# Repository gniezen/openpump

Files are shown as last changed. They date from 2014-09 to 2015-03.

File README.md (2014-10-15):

# Openpump: the open source hardware syringe pump

[Openpump](http://www.openpump.org) is an open-source syringe pump that dispenses fluids over a set period of time. Syringe pumps are used to administer medication in hospitals, but also in laboratory environments performing chemical or biomedical research. Maybe you'd like to use syringe pump to extruding paste (e.g. chocolate) during 3D printing, or as part of a bioprinter when printing with biological materials?

Openpump is a collaboratively designed general-purpose syringe pump platform that can be customised for different domains. Making the hardware design available under an open source license allows anyone to improve and contribute to the device design. It also enables the design to be modified for very specific use cases and makes the devices easy to repair.

## Setup

### Rendering the 3D parts

The mechanical/CAD design of Openpump is based on work by Bas Wijnen, Emily Hunt, Gerald Anzalone and Joshua Pearce of  [Michigan Tech Open Sustainaibility Lab](http://www.appropedia.org/Open-source_syringe_pump). The 3D-printed parts were designed in [OpenSCAD](http://www.openscad.org/). (To learn how to use OpenSCAD, see [the Openpump blog](http://blog.openpump.org/how-to-design-a-3d-printed-enclosure-for-your-product/)). To render the different 3D parts in `linear_actuator_v0.scad`:

* Install the [MOST SCAD libraries](https://github.com/mtu-most/most-scad-libraries) by downloading them as a zip file and adding to OpenSCAD path using `export OPENSCADPATH=`<*your local path*> (in `~/.profile` on Ubuntu), or using `File->Show Library Folder` to add them to your OpenSCAD library.
* Change `render_part()` to the 3D part you want to render. You need `end_motor` (1), `end_idler` (2), `carriage_syringe_pump` (4), `clamp_syringe_pump` (5) and `syringe_plunger_retainer` (7) at a minimum.
* Before printing the syringe holder (part 5, `clamp_syringe_pump`), set the variable `d_syringe` to the be the same as the diameter of the syringe body you're using.
* Before printing the motor end (part 1, `end_motor`) set the `motor` variable to the size of stepper motor you're using, e.g. `NEMA17`
* I had best results printing the idler end (part 2, `end_idler`) with support material.

### Building the mechanical design
The step-by-step build instructions with pictures are in the [Building the syringe pump guide](http://openpump.dozuki.com/c/Build_instructions).

### Building the electronics
To build the electronics, you need the following components:
* [Arduino Mega 2560](http://arduino.cc/en/Main/ArduinoBoardMega2560) (You can also use another Arduino, but you'll need something like the Sparkfun [ProtoScrewShield](https://www.sparkfun.com/products/9729) to connect the other components as the Gameduino 2 shield covers all the pins of the regular Arduino)
* [Gameduino 2](http://excamera.com/sphinx/gameduino2/), an open source hardware touchscreen (480x272 pixels) with embedded GPU
* [Pololu DRV8834](http://www.pololu.com/product/2134) Low Voltage Stepper Motor Driver Board (You're welcome to replace this with another board if you know what you're doing)
* [ELMA E37](http://www.leobodnar.com/shop/index.php?main_page=product_info&cPath=75&products_id=196) dual concentric rotary encoder (kinda optional, used for number entry)

Because the Mega2560 has its SPI pins in a different place, you need to make 3 wire hookups. Connect:
- pin 11 to pin 51 (MOSI)
- pin 12 to pin 50 (MISO)
- pin 13 to pin 52 (SCK)

You can solder these three wires directly to the pins underneath the Mega.

To view the circuit schematic (with breadboard views), use the awesome open source hardware design tool [Fritzing](http://fritzing.org/).

## Installing the firmware

To get the firmware running on your Arduino, have a look at the documentation in the [firmware](firmware/) folder. 

## Licenses

### Software and firmware
The software and firmware of this project is *Copyright (C) 2014 Swansea University* and made available under the GNU Affero General Public License (AGPL 3.0). See LICENSE.txt in the firmware folder for more information.

### Mechanical design
The CAD design file (linear_actuator_v0.scad) is *Copyright 2013 Michigan Technological University* and licensed under the [CC-BY-SA](Creative Commons Attribution-ShareAlike 4.0 International License) by Jerry Anzalone, developed as part of a project with the [Michigan Tech Open Sustainability Technology Research Group](http://www.appropedia.org/Category:MOST).

### Circuit schematics
The circuit schematics of this project are made available under the [CERN Open Hardware License](http://www.ohwr.org/projects/cernohl/wiki). See LICENSE.PDF in the schematics folder for more information.

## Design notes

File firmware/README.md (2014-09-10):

# Openpump: Firmware

## Setup

To get this up and running in your Arduino environment, you need two libraries:
- [Encoder](https://www.pjrc.com/teensy/td_libs_Encoder.html)
- [Gameduino 2](http://excamera.com/files/Gameduino2.zip)

Install it in the Arduino environment using the [official instructions](http://arduino.cc/en/Guide/Libraries).

## Working with Gameduino 2
If you want to create your own assets for Gameduino 2, follow the setup instructions below and also see the instruction on the [Gameduino 2 website](http://excamera.com/sphinx/gameduino2/code.html#gd2code). 

### Library setup
Prerequisites:
- Install PIL using `sudo pip install pil` 
- Install Gameduino 2 asset converter and Python libraries using `sudo pip install gameduino2`

Note: On Mac you can also install `sudo pip install pillow` and port Gameduino 2 to use Pillow instead of PIL: http://pillow.readthedocs.org/en/latest/porting-pil-to-pillow.html

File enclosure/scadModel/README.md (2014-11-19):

# OpenSCAD OpenPump Enclosure

This design makes use of the [Arduino OpenSCAD mounting library (v2.0)](http://www.thingiverse.com/thing:64008) by Kelly Egan.

To create the enclosure:

	enclosure(MEGA2560);

To create the lid:

	enclosureLid(MEGA2560);

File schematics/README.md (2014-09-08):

# Openpump: Circuit Schematics

Copyright Swansea University 2014.

This documentation describes Open Hardware and is licensed under the
CERN OHL v. 1.2.

You may redistribute and modify this documentation under the terms of the CERN OHL v.1.2. (http://ohwr.org/cernohl). This documentation is distributed WITHOUT ANY EXPRESS OR IMPLIED WARRANTY, INCLUDING OF MERCHANTABILITY, SATISFACTORY QUALITY AND FITNESS FOR A PARTICULAR PURPOSE. Please see the CERN OHL v.1.2 for applicable conditions

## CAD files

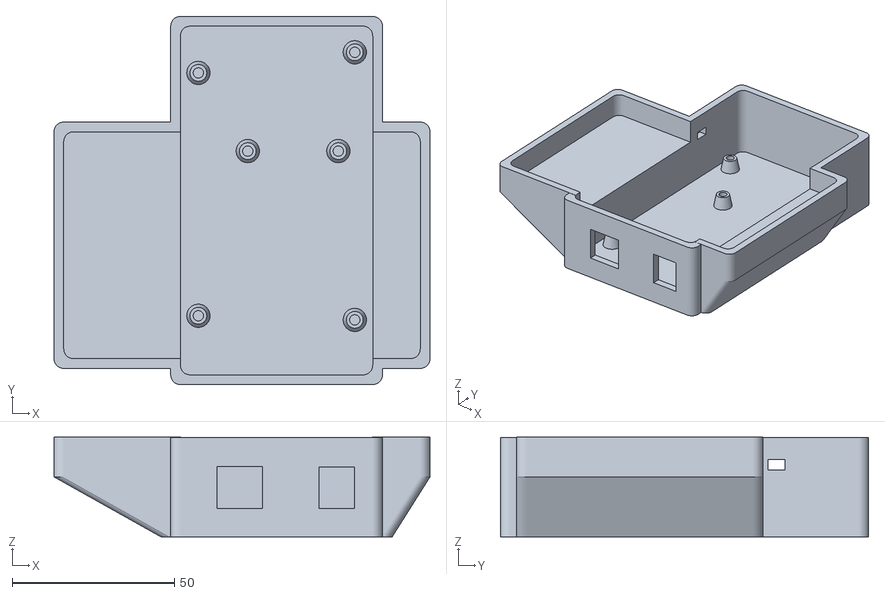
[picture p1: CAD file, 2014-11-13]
enclosure/scadModel/openPumpBox.stl
116.0 x 113.6 x 30.8

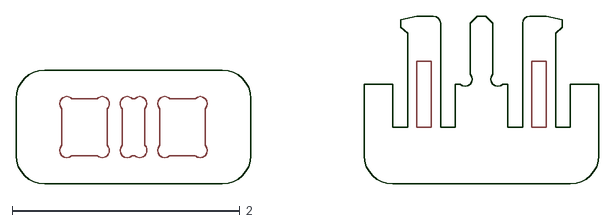
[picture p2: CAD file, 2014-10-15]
enclosure/snap.dxf
5.12 x 1.48

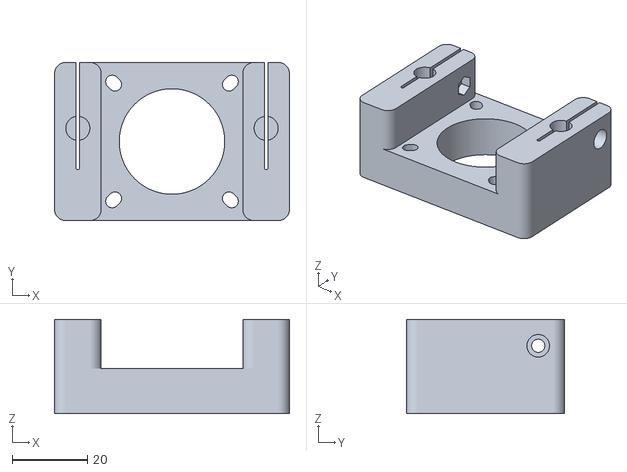
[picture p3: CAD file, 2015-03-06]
mechanical/1_end_motor.stl
62.4 x 42.0 x 25.0

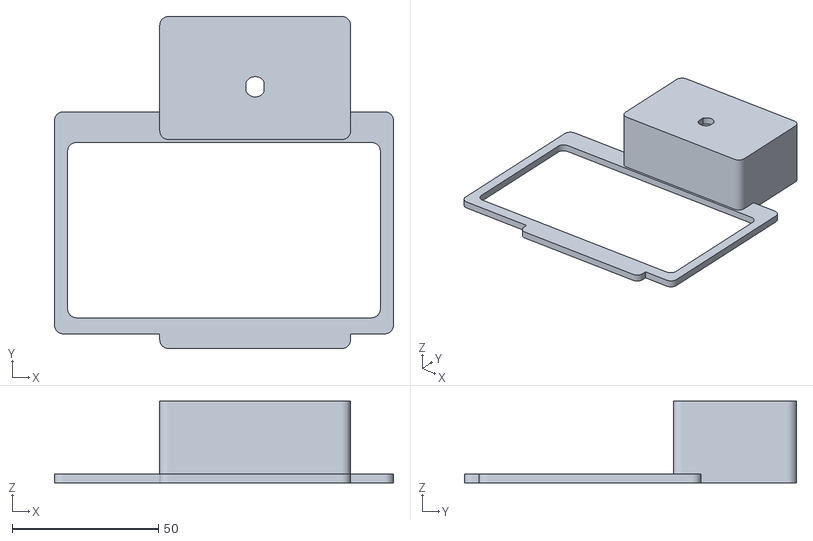
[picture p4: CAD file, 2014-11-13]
enclosure/scadModel/openPumpLid.stl
116.0 x 113.6 x 28.0

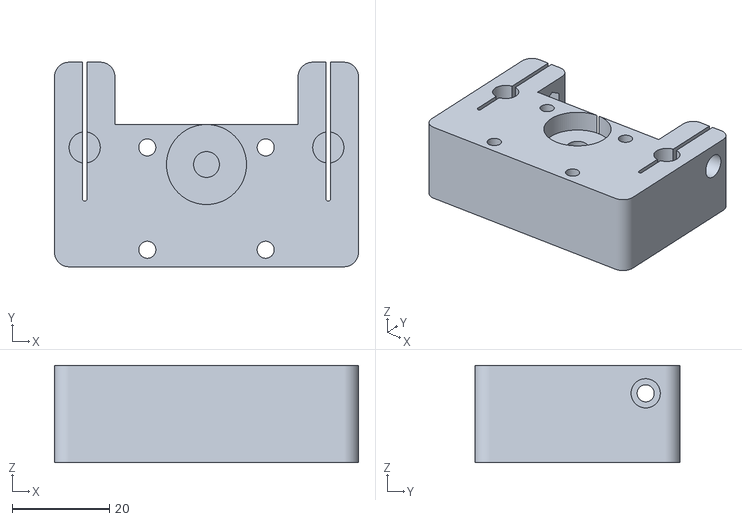
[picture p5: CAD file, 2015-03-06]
mechanical/2_end_idler.stl
62.4 x 42.0 x 20.0

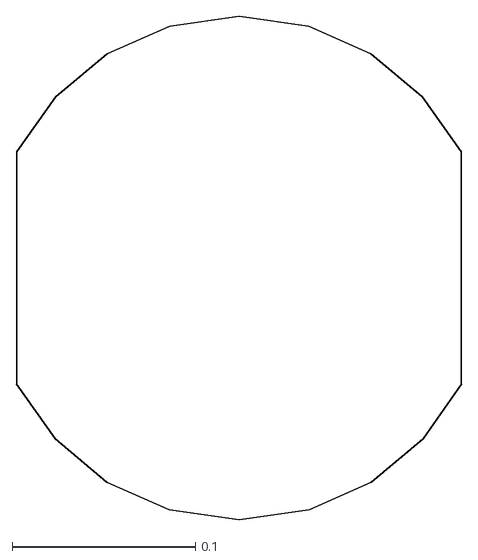
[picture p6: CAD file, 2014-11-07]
enclosure/scadModel/rotary.dxf
0.243 x 0.275

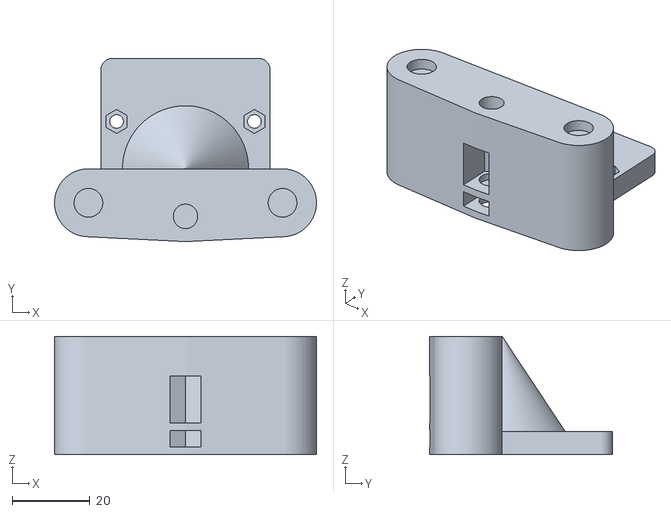
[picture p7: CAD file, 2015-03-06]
mechanical/4_carriage_syringe_pump.stl
67.5 x 47.2 x 30.5

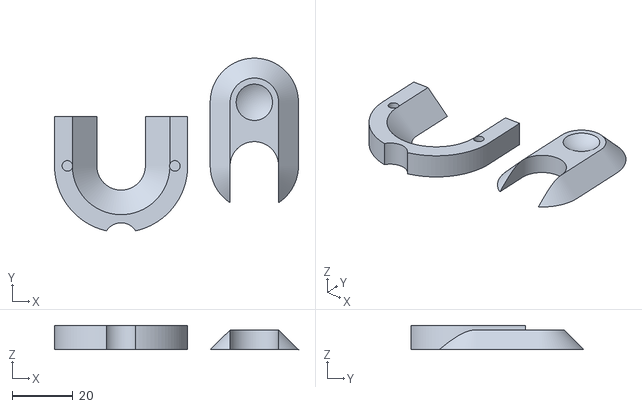
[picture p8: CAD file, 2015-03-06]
mechanical/7_syringe_plunger_retainer.stl
80.6 x 57.0 x 8.00

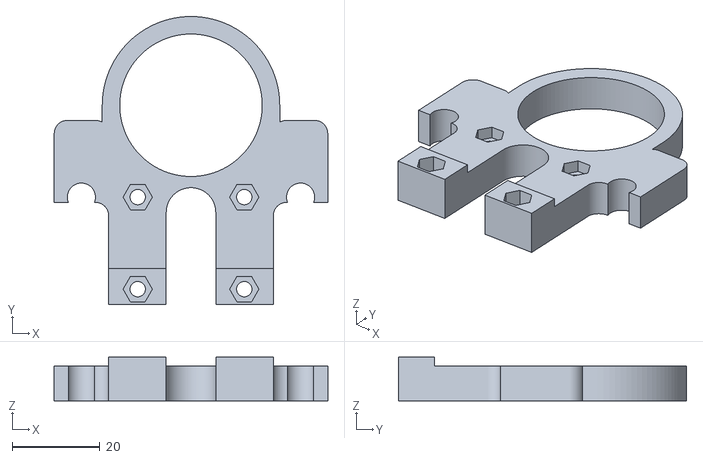
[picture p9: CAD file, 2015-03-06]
mechanical/5_clamp_syringe_pump.stl
62.4 x 65.7 x 10.0

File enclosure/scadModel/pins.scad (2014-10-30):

// Pin Connectors V3
// Tony Buser <tbuser@gmail.com>
// Modified by Emmett Lalish

object=4;//[0:pin,1:pinpeg,2:pinhole,4:nothing]
length=20;
diameter=8;
//Only affects pinhole
hole_twist=0;//[0:free,1:fixed]
//Only affects pinhole
hole_friction=0;//[0:loose,1:tight]
//Radial gap to help pins fit into tight holes
pin_tolerance=0.2;
//Extra gap to make loose hole
loose=0.3;
lip_height=3;
lip_thickness=1;
hf=hole_friction==0 ? false : true;
ht=hole_twist==0 ? false : true;

if(object==0)pin(h=length,r=diameter/2,lh=lip_height,lt=lip_thickness,t=pin_tolerance);
if(object==1)pinpeg(h=length,r=diameter/2,lh=lip_height,lt=lip_thickness,t=pin_tolerance);
if(object==2)pinhole(h=length,r=diameter/2,lh=lip_height,lt=lip_thickness,t=loose,
	tight=hf,fixed=ht);

module test() {
  tolerance = 0.3;
  
  translate([-12, 12, 0]) pinpeg(h=20);
  translate([12, 12, 0]) pintack(h=10);
  
  difference() {
    union() {
      translate([0, -12, 2.5]) cube(size = [59, 20, 5], center = true);
      translate([24, -12, 7.5]) cube(size = [12, 20, 15], center = true);
    }
    translate([-24, -12, 0]) pinhole(h=5, t=tolerance);
    translate([-12, -12, 0]) pinhole(h=5, t=tolerance, tight=false);
    translate([0, -12, 0]) pinhole(h=10, t=tolerance);
    translate([12, -12, 0]) pinhole(h=10, t=tolerance, tight=false);
    translate([24, -12, 15]) rotate([0, 180, 0]) pinhole(h=10, t=tolerance);
  }
}

module pinhole(h=10, r=4, lh=3, lt=1, t=0.3, tight=true, fixed=false) {
  // h = shaft height
  // r = shaft radius
  // lh = lip height
  // lt = lip thickness
  // t = extra tolerance for loose fit
  // tight = set to false if you want a joint that spins easily
  // fixed = set to true so pins can't spin
  
intersection(){
  union() {
	if (tight == true || fixed == true) {
      pin_solid(h, r, lh, lt);
	  translate([0,0,-t/2])cylinder(h=h+t, r=r, $fn=30);
	} else {
	  pin_solid(h, r+t/2, lh, lt);
	  translate([0,0,-t/2])cylinder(h=h+t, r=r+t/2, $fn=30);
	}
    
    
    // widen the entrance hole to make insertion easier
    //translate([0, 0, -0.1]) cylinder(h=lh/3, r2=r, r1=r+(t/2)+(lt/2),$fn=30);
  }
  if (fixed == true) {
	translate([-r*2, -r*0.75, -1])cube([r*4, r*1.5, h+2]);
  }
}}

module pin(h=10, r=4, lh=3, lt=1, t=0.2, side=false) {
  // h = shaft height
  // r = shaft radius
  // lh = lip height
  // lt = lip thickness
  // side = set to true if you want it printed horizontally

  if (side) {
    pin_horizontal(h, r, lh, lt, t);
  } else {
    pin_vertical(h, r, lh, lt, t);
  }
}

module pintack(h=10, r=4, lh=3, lt=1, t=0.2, bh=3, br=8.75) {
  // bh = base_height
  // br = base_radius
  
  union() {
    cylinder(h=bh, r=br);
    translate([0, 0, bh]) pin(h, r, lh, lt, t);
  }
}

module pinpeg(h=20, r=4, lh=3, lt=1, t=0.2) {
  union() {
    translate([0,-0.05, 0]) pin(h/2+0.1, r, lh, lt, t, side=true);
    translate([0,0.05, 0]) rotate([0, 0, 180]) pin(h/2+0.1, r, lh, lt, t, side=true);
  }
}

// just call pin instead, I made this module because it was easier to do the rotation option this way
// since openscad complains of recursion if I did it all in one module
module pin_vertical(h=10, r=4, lh=3, lt=1, t=0.2) {
  // h = shaft height
  // r = shaft radius
  // lh = lip height
  // lt = lip thickness

  difference() {
    pin_solid(h, r-t/2, lh, lt);
    
    // center cut
    translate([-lt*3/2, -(r*2+lt*2)/2, h/5+lt*3/2]) cube([lt*3, r*2+lt*2, h]);
    //translate([0, 0, h/4]) cylinder(h=h+lh, r=r/2.5, $fn=20);
    // center curve
    translate([0, 0, h/5+lt*3/2]) rotate([90, 0, 0]) cylinder(h=r*2, r=lt*3/2, center=true, $fn=20);
  
    // side cuts
    translate([-r*2, -r-r*0.75+t/2, -1]) cube([r*4, r, h+2]);
    translate([-r*2, r*0.75-t/2, -1]) cube([r*4, r, h+2]);
  }
}

// call pin with side=true instead of this
module pin_horizontal(h=10, r=4, lh=3, lt=1, t=0.2) {
  // h = shaft height
  // r = shaft radius
  // lh = lip height
  // lt = lip thickness
  translate([0, 0, r*0.75-t/2]) rotate([-90, 0, 0]) pin_vertical(h, r, lh, lt, t);
}

// this is mainly to make the pinhole module easier
module pin_solid(h=10, r=4, lh=3, lt=1) {
  union() {
    // shaft
    cylinder(h=h-lh, r=r, $fn=30);
    // lip
    // translate([0, 0, h-lh]) cylinder(h=lh*0.25, r1=r, r2=r+(lt/2), $fn=30);
    // translate([0, 0, h-lh+lh*0.25]) cylinder(h=lh*0.25, r2=r, r1=r+(lt/2), $fn=30);
    // translate([0, 0, h-lh+lh*0.50]) cylinder(h=lh*0.50, r1=r, r2=r-(lt/2), $fn=30);

    // translate([0, 0, h-lh]) cylinder(h=lh*0.50, r1=r, r2=r+(lt/2), $fn=30);
    // translate([0, 0, h-lh+lh*0.50]) cylinder(h=lh*0.50, r1=r+(lt/2), r2=r-(lt/3), $fn=30);    

    translate([0, 0, h-lh]) cylinder(h=lh*0.25, r1=r, r2=r+(lt/2), $fn=30);
    translate([0, 0, h-lh+lh*0.25]) cylinder(h=lh*0.25, r=r+(lt/2), $fn=30);    
    translate([0, 0, h-lh+lh*0.50]) cylinder(h=lh*0.50, r1=r+(lt/2), r2=r-(lt/2), $fn=30);    

    // translate([0, 0, h-lh]) cylinder(h=lh, r1=r+(lt/2), r2=1, $fn=30);
    // translate([0, 0, h-lh-lt/2]) cylinder(h=lt/2, r1=r, r2=r+(lt/2), $fn=30);
  }
}

module pinshaft(h=10, r=4, t=0.2, side=false){
flip=side ? 1 : 0;
translate(flip*[0,h/2,r*0.75-t/2])rotate(flip*[90,0,0])
intersection(){
	cylinder(h=h, r=r-t/2, $fn=30);
	translate([-r*2, -r*0.75+t/2, -1])cube([r*4, r*1.5-t, h+2]);
}
}

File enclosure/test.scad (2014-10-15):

dxf_linear_extrude(file="snap.dxf", height=0.5);

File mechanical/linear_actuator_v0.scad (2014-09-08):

// Copyright 2013 Michigan Technological University
// Author: Jerry Anzalone
// This design was developed as part of a project with
// the Michigan Tech Open Sustainability Technology Research Group
// http://www.appropedia.org/Category:MOST
// It is released under CC-BY-SA

include<fasteners.scad>
include<steppers.scad>
include<bearings.scad>

$fn = 96;

render_part(5);

module render_part(part_to_render) {
	if (part_to_render == 1) end_motor();

	if (part_to_render == 2) end_idler();

	if (part_to_render == 3) carriage();

	if (part_to_render == 4) carriage_syringe_pump();

	if (part_to_render == 5) clamp_syringe_pump();

	if (part_to_render == 6) {
		for (i = [-1, 1])
			translate([i * (d_guide_rod + 2.5), 0, 0])
				syringe_hook();
	}

	if (part_to_render == 7) {syringe_plunger_retainer();}

	if (part_to_render == 8) syringe_bungie();
}

// [x, y, z] = [l, w, t]

/*

No moving motor!
Simple loading
Simple cleaning
Protect motor
Secure plunger

*/

d_nozzle = 0.75;

motor = NEMA17;
cc_guides = 50;

d_lead_screw = d_M5_screw;
d_lead_nut = d_M5_nut;
h_lead_nut = h_M5_nut;
od_antibacklash_spring = 7;
l_antibacklash_spring = 10;

offset_guides = 3.5; // offset from centerline of motor shaft towards top (+y)
d_guide_rod = 6.4; // 6mm guide rods
guide_bearing = bearing_lm6uu;
pad_guide_bearing_radius = 3;

pad_guide_ends = 3; // backing material behind ends of guide rods
pad_guide_radius = 3; // material surrouding guide rods and bearings
t_motor_mount = 12;
w_ends = motor[0];
l_ends = cc_guides + d_guide_rod + 2 * pad_guide_radius;
xy_aspect = l_ends / w_ends; // needed to scale rounded box
t_motor_end = 25;
idler = bearing_625;
t_idler_end = 20;

t_carriage = guide_bearing[2] + 6;

d_clamp_screw = d_M3_screw;
d_clamp_screw_cap = d_M3_cap;
d_clamp_screw_nut = d_M3_nut;

// following for attachments


// syringe pump:
d_plunger = 32; // diameter of the plunger end
d_syringe = 32.5; // diameter of the syringe body - sets size of syringe holder
t_hook = 5; // thickness of the hook for securing syringe to actuator
d_plunger_max = 32; // this sets the spacing for screws on the plunger retainer and carriage
d_plunger_retainer = d_plunger_max + 12;


module end_motor() {
	difference() {
		union() {
			rod_clamps(t_motor_end, pad_guide_ends);

			// motor plate
			difference () {
				translate([0, 0, (t_motor_mount - t_motor_end) / 2])
					cube([l_ends - (l_ends - cc_guides) - 1, w_ends, t_motor_mount], center = true);

				clamp_relief(t_motor_end, pad_guide_ends);
			}
		}

		// motor mount holes
		translate([0, 0, -t_motor_end / 2])
			rotate([0, 0, 45])
				NEMA_X_mount(
					height = t_motor_end,
					l_slot = 1,
					motor = motor);

		// keyhole opening for motor mount screws
		// for (i = [-1, 1])
		//	translate([i * motor[3] / 2, -motor[3] / 2, 0])
		//		cylinder(r = 2.5, h = 5, center = true);
	}
}

module end_idler() {
	difference() {
		union() {
			rod_clamps(t_idler_end, pad_guide_ends);

			// idler bearing housing

			difference () {
				translate([0, -((w_ends + idler[0]) / 2 - idler[0]) / 2, 0])
					cube([l_ends - (l_ends - cc_guides), (w_ends + idler[0]) / 2, t_idler_end], center = true);

				clamp_relief(t_motor_end, pad_guide_ends);
			}

		}

		// outboard idler bearing
		translate([0, 0, -t_idler_end / 2])
			cylinder(r = idler[0] / 2 + 0.01, h = idler[2] * 2, center = true);

		// inboard idler bearing
		translate([0, 0, t_idler_end / 2])
			cylinder(r = idler[0] / 2 + 0.01, h = idler[2] * 2, center = true);

		// lead screw
		translate([0, 0, idler[2] + 0.2])
			cylinder(r = d_lead_screw / 2, h = t_idler_end, center = true);

		end_mount_holes(t_idler_end + 1, d_M3_screw);
	}	
}

module carriage_body() {
	hull() {
		for (i = [-1, 1])
			translate([i * cc_guides / 2, offset_guides, 0])
				cylinder(r = guide_bearing[0] / 2 + pad_guide_bearing_radius, h = t_carriage, center = true);

		cylinder(r = od_antibacklash_spring / 2 + pad_guide_radius, h = t_carriage, center = true);
	}
}

module carriage_relief() {
	for (i = [-1, 1])
		translate([i * cc_guides / 2, offset_guides, 0]) {
			// guide rods
			cylinder(r = d_guide_rod / 2 + 0.5, h = t_carriage + 2, center = true);

			// guide bearings
			cylinder(r = guide_bearing[0] / 2, h = guide_bearing[2], center = true);

			translate([i * (guide_bearing[0] / 2 - 2), -(guide_bearing[0] / 2 - 2), , 0])
				cylinder(r = guide_bearing[0] / 2, h = guide_bearing[2], center = true);
	}

	// nut trap for fixed nut
	hull()
		for (i = [0, -1])
			translate([0, i * t_carriage, -t_carriage / 2 + 2])
				rotate([0, 0, 30])
					cylinder(r = d_lead_nut / 2, h = h_lead_nut, $fn = 6);

	// lead nuts and anti-backlash spring
	hull()
		for (i = [0, 1])
			translate([0, i * -20, -t_carriage / 2 + h_lead_nut + 4])
				rotate([0, 0, 30])
					cylinder(r = d_lead_nut / 2, h = l_antibacklash_spring + h_lead_nut / 2, $fn = 6);

	translate([0, 0, -t_carriage / 2 + h_lead_nut + 4])
		rotate([0, 0, 30])
			cylinder(r = d_lead_nut / 2, h = l_antibacklash_spring + h_lead_nut, $fn = 6);

	// lead screw
	cylinder(r = d_lead_screw /2 + 0.5, h = t_carriage + 2, center = true);
}

module carriage_support() {
	// floors for holes
	for (i =[-1, 1])
		translate([i * cc_guides / 2, offset_guides, guide_bearing[2] / 2])
			cylinder(r = guide_bearing[0] / 2 - 1, h = 0.2);

	translate([0, 0, -t_carriage / 2 + h_lead_nut + 4 + l_antibacklash_spring + h_lead_nut])
		cylinder(r = d_lead_nut / 2, h = 0.2);

	translate([0, 0, -t_carriage / 2 + h_lead_nut + 4 + l_antibacklash_spring + h_lead_nut / 2])
		cylinder(r = d_lead_nut / 2 + 1, h = 0.2);

	translate([0, 0, -t_carriage / 2 + 2 + h_lead_nut])
		cylinder(r = d_lead_nut / 2 + 1, h = 0.2);

	// filler for gaps
	for (i =[-1, 1])
		translate([i * cc_guides / 2, offset_guides, 0])

			difference() {
				cylinder(r = guide_bearing[0] / 2 + pad_guide_bearing_radius, h = t_carriage, center = true);

				cylinder(r = guide_bearing[0] / 2 + pad_guide_bearing_radius - d_nozzle, h = t_carriage + 2, center = true); 
			}
}

module carriage() {
	union() {
		difference() {
			carriage_body();

			carriage_relief();
		}

		carriage_support();
	}
}

module rounded_box(
	l1,
	l2,
	r_corner,
	height) {

	hull()
		for (i = [-1, 1])
			for (j = [-1, 1])
				translate([i * (l1 / 2 - r_corner), j * (l2 / 2 - r_corner), 0])
					cylinder(r = r_corner, h = height, center = true);
}

module clamp_body(thickness) {
	union() {
		for (i = [-1, 1])
			translate([i * cc_guides / 2, 0, 0])
				rounded_box(
					l1 = (l_ends - cc_guides),
					l2 = w_ends,
					r_corner = 3,
					height = thickness);

		// bottom
		//translate([0, (4 - w_ends) / 2, 0]) cube([cc_guides, 4, thickness], center = true);
	}
}

module clamp_relief(
	thickness,
	pad_ends) {
			// guide rods have backing, so are off the end of the body
			for (i = [-1, 1])
				translate([i * cc_guides / 2, offset_guides, pad_ends])
					cylinder(r = d_guide_rod / 2, h = thickness, center = true);

			// slots for clamping guide rods
			for (i = [-1, 1])
				translate([i * cc_guides / 2, offset_guides, 0])
					hull()
						for (j = [-0.25, 1])
							translate([0, j * w_ends, 0])
								cylinder(r = 0.5, h = thickness + 2, center = true);

			// holes for clamp screws
			translate([0, w_ends / 4 + offset_guides, 0]) {
				for (i = [-1, 1])
					for (j = [1]) {
						translate([i * cc_guides / 2, 0, j * (thickness - pad_ends) / 4])
							rotate([0, 90, 0])
								cylinder(r = d_clamp_screw / 2, h = (l_ends - cc_guides) * 2, center = true);

						translate([i * l_ends / 2, 0, j * (thickness - pad_ends) / 4])
							rotate([0, 90, 0])
								cylinder(r = d_clamp_screw_cap / 2, h = 8, center = true);

						translate([0, 0, j * (thickness - pad_ends) / 4])
							rotate([0, 90, 0])
								cylinder(r = d_clamp_screw_nut / 2, h = cc_guides - (l_ends - cc_guides) / 2, $fn = 6, center = true);
					}
			}

}

module rod_clamps(
	thickness,
	pad_ends) {
	difference() {
		clamp_body(thickness);

		clamp_relief(thickness, pad_ends);
	}
}

module end_mount_holes(
	thickness,
	diameter,
	fn = $fn) {
	// screw holes for retaining items against clamp
	for (i = [-1, 1])
		for (j = [-1, 0])
			translate([i * (cc_guides - idler[0] - d_lead_nut) / 2, offset_guides + j * w_ends / 2, 0])
				cylinder(r = diameter / 2, h = thickness, $fn = fn, center = true);
}

/****************************

 following are attachments for the base linear actuator

****************************/

// renders a carriage with a pusher attachement and place to fix a locking cam
module carriage_syringe_pump() {
	t_holder = 6; // thickness of the cylindrical portion of the pusher

	union() {
		difference() {
			union() {
				carriage_body();

				// pusher for the plunger
				translate([0, (idler[0] + d_syringe) / 2, (t_holder - t_carriage) / 2])
					rounded_box(
						l1 = cc_guides - d_guide_rod,
						l2 = d_syringe,
						r_corner = 3,
						height = t_holder);
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

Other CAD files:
enclosure/scadModel/scadModel.stl
enclosure/scadModel/arduino.scad

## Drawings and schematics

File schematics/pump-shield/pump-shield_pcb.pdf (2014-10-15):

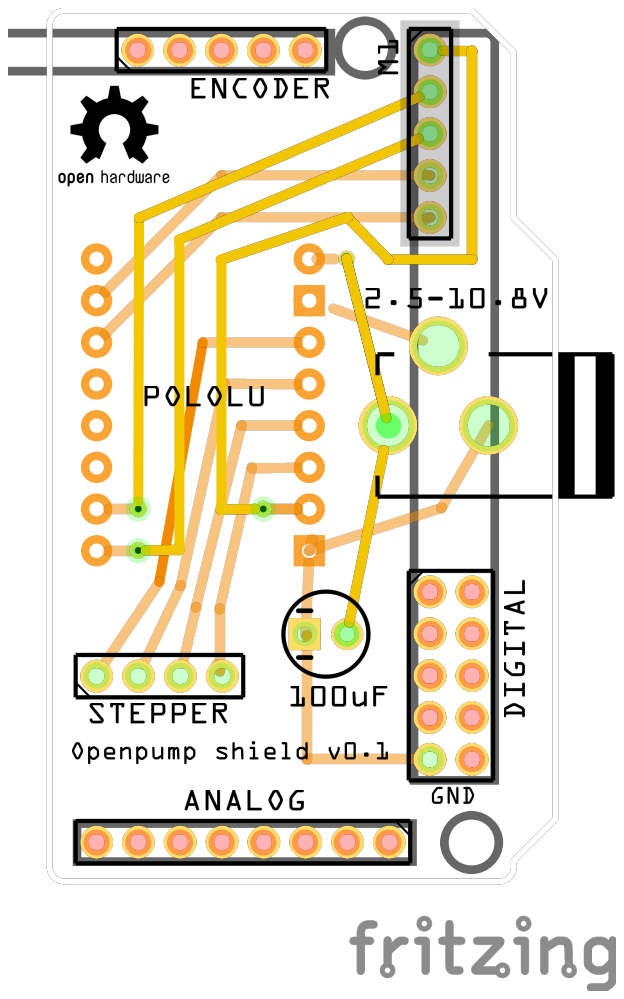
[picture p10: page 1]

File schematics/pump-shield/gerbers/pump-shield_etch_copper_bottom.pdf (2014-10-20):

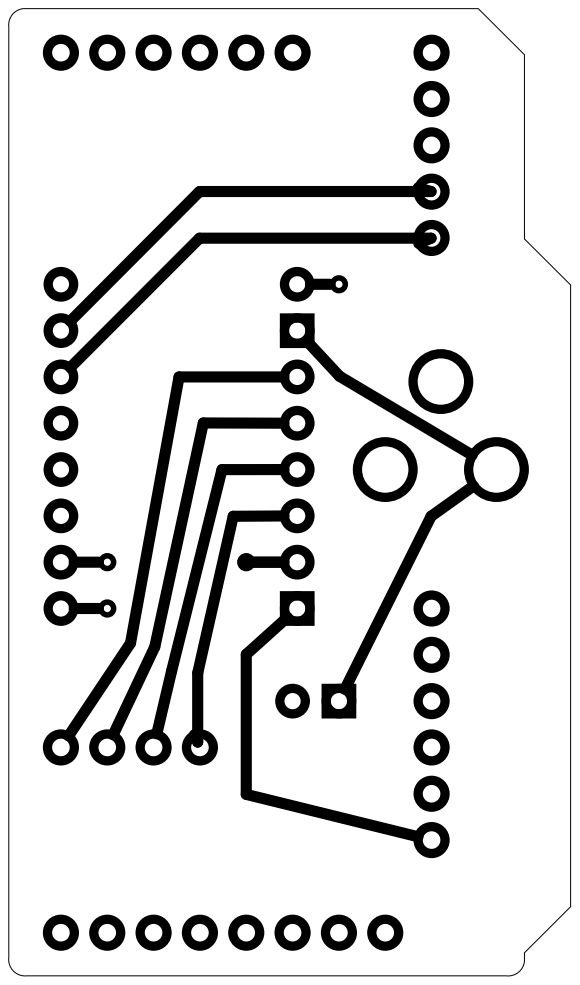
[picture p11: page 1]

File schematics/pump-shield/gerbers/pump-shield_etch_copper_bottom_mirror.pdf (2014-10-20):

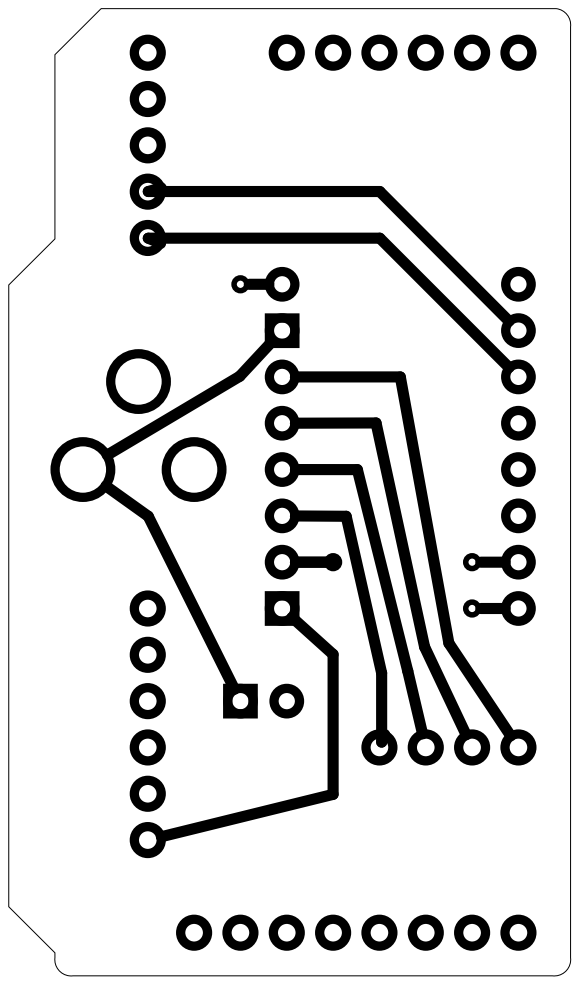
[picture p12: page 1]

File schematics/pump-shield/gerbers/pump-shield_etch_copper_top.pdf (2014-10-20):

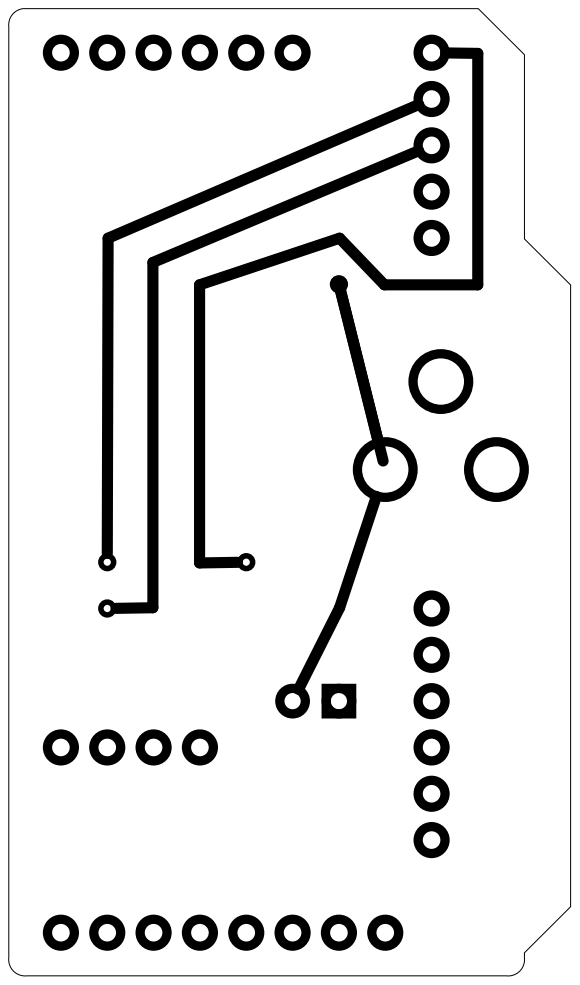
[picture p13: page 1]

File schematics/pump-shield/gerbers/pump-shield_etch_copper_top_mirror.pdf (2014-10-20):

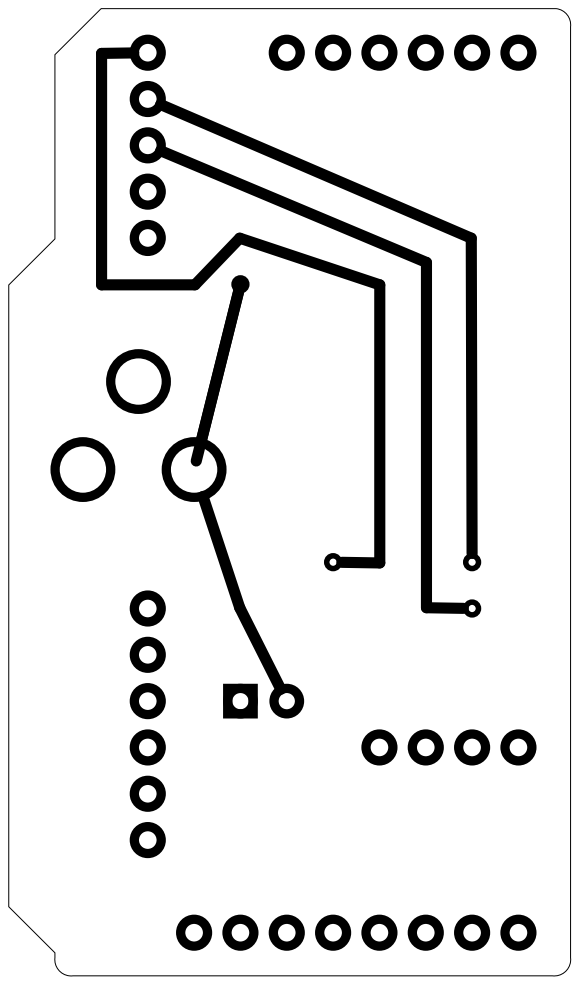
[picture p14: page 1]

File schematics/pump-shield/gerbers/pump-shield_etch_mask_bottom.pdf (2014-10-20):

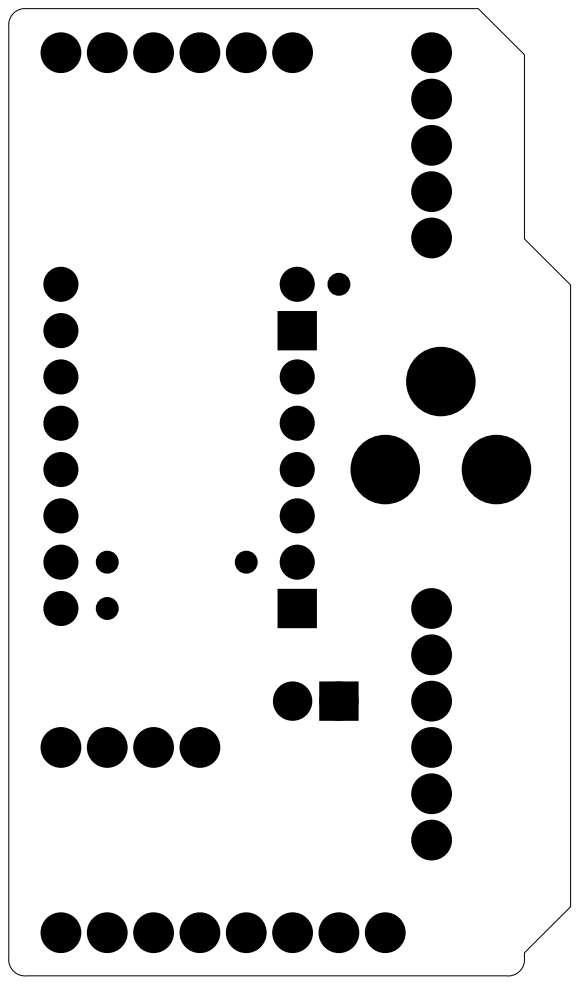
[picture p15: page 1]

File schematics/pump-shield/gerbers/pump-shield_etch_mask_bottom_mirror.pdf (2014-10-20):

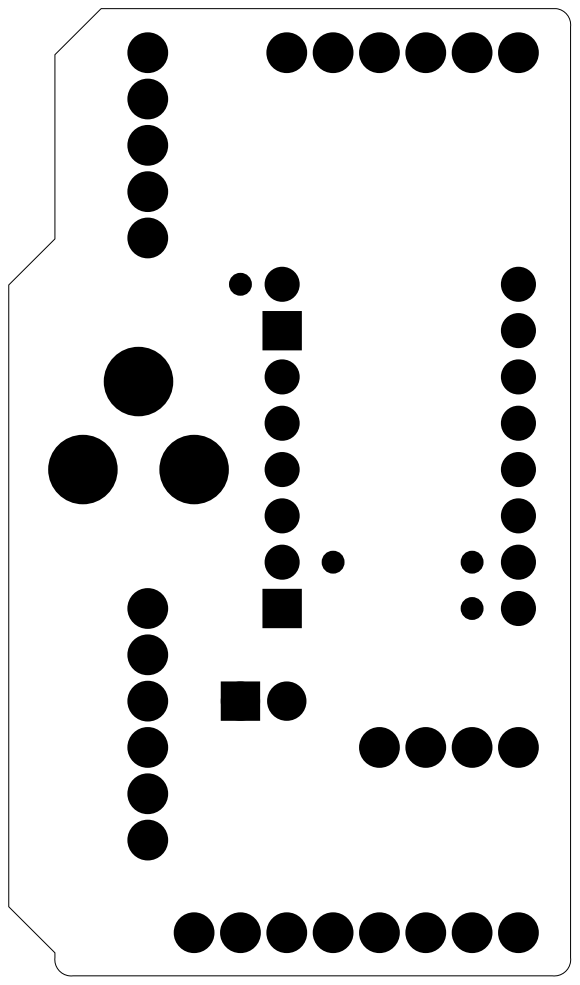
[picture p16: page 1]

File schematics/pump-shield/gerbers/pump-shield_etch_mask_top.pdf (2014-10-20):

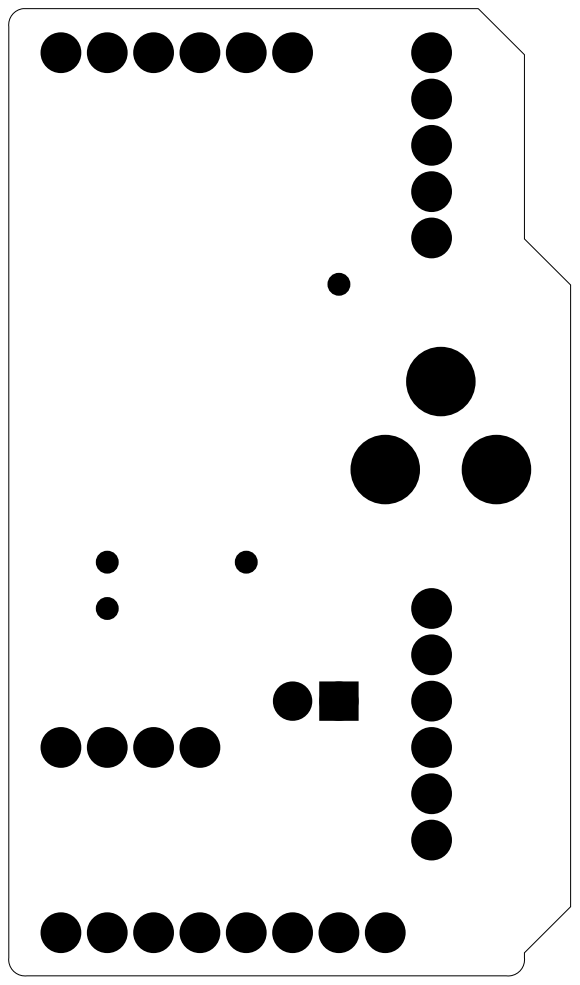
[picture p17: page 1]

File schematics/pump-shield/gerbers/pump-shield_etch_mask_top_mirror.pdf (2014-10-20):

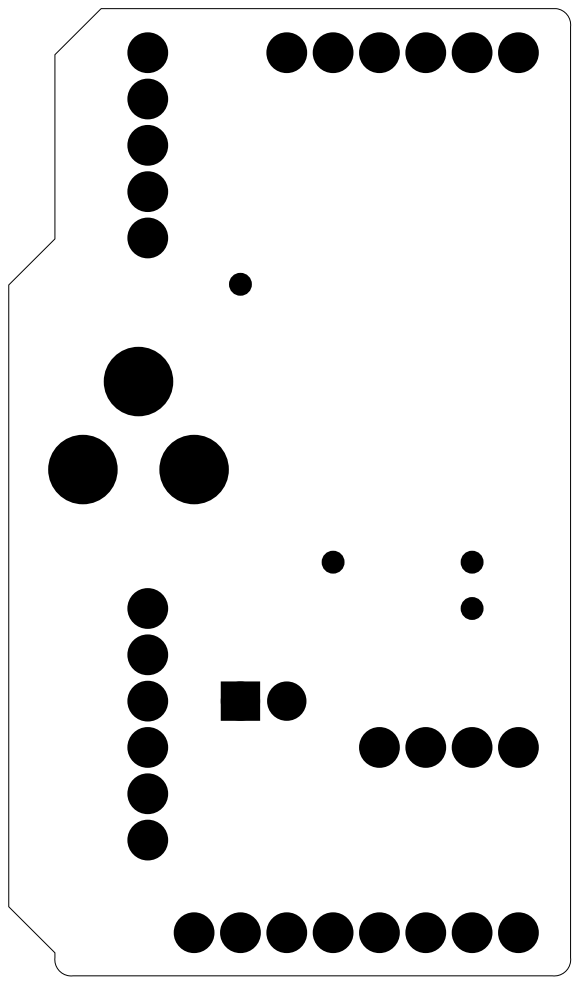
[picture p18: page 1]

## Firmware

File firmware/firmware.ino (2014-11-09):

/*
    Openpump Firmware
    Copyright (C) 2014 Swansea University

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
    You should have received a copy of the GNU Affero General Public License
    along with this program.  If not, see <http://www.gnu.org/licenses/>.
*/

#include <EEPROM.h>
#include <SPI.h>
#include <GD2.h>
#include <Encoder.h>

#include "default_assets.h"

int dirpin =  24; 
int steppin = 22;

// Rotary encoder best performance: both pins have interrupt capability
Encoder knobLeft(18, 19);
Encoder knobRight(20, 21);

int i = 0;
int pressed = 0;
long positionLeft  = -999;
long positionRight = -999;

long timeBetweenSteps = 1000;  // in ms
long previousMillis = 0;

boolean running, reversing = false;

void setup()
{
  // Set up stepper motor driver
  pinMode(dirpin, OUTPUT);     
  pinMode(steppin, OUTPUT);
  
  //Set up graphics
  GD.begin();
  LOAD_ASSETS();
}

void loop()
{
  // Read rotary encoder
  long newLeft, newRight;
  newLeft = knobLeft.read();
  newRight = knobRight.read();
  if (newLeft != positionLeft || newRight != positionRight) {

    if(newLeft <= 0) {
      newLeft = 0;
      knobLeft.write(0);
    }
    if(newRight <= 0) {
      newRight = 0;
      knobRight.write(0);  
    }
    
    if(newRight > 198) {
      newRight = 198;
      knobRight.write(198);
    }
    
    positionLeft = newLeft;
    positionRight = newRight;  

  }

  //Drive stepper motor
  
  if(reversing) {
    digitalWrite(dirpin, LOW);     // Set the direction backward
    
    for(int i=0;i<1000;i++) {
      digitalWrite(steppin, LOW);
      delayMicroseconds(2); //motor speed  
      digitalWrite(steppin, HIGH); // Creates 'rising edge'
      delayMicroseconds(1000); //motor speed 
    }
  } 
  
  unsigned long currentMillis = millis();
  if(running && !reversing) {
    
    digitalWrite(dirpin, HIGH);     // Set the direction forward
    
    if(currentMillis - previousMillis > (timeBetweenSteps-positionLeft)) {

      previousMillis = currentMillis;
    
      for (int i = 0; i<20; i++)     // number of microsteps at one time  
      {
        digitalWrite(steppin, LOW);
        delayMicroseconds(2);   
        digitalWrite(steppin, HIGH); // Creates 'rising edge'
        delayMicroseconds(1000); //motor speed     
      }
    }
  }
  
  // Graphics
  
  GD.get_inputs();
  GD.Clear();
  plotRate(110,68,positionLeft/2,positionRight/2);
    
  //GD.cmd_button(20,150,190,50,28,OPT_FLAT,"Button");
  
  GD.Begin(BITMAPS);
  
  pressed = GD.inputs.tag;
  
  int offset1, offset2,offset3=0;
  
  //Start button
  GD.Tag(1);
  if(pressed == 1) {
    GD.Vertex2ii(70,174,BUTTON1_HANDLE);
    offset1=4;
    running = true;
  }else{
    GD.Vertex2ii(70,170,BUTTON0_HANDLE);
    offset1=0;
  }
  GD.Vertex2ii(85,175+offset1,START_HANDLE);
  GD.cmd_text(185,185+offset1, 29, OPT_CENTERX,"Start");
  
  //Stop button
  GD.Tag(2);
  GD.ColorRGB(0xff2e18);
  if(pressed == 2) {
    GD.Vertex2ii(280,174,BUTTON1_HANDLE);
    offset2=4;
    running = false;
  }else{
    GD.Vertex2ii(280,170,BUTTON0_HANDLE);
    offset2=0;
  }
  GD.ColorRGB(0xffffff);
  GD.Vertex2ii(295,175+offset2,STOP_HANDLE);
  GD.cmd_text(395, 185+offset2, 29, OPT_CENTERX,"Stop");
  
  //Reverse button
  GD.Tag(3);
  GD.ColorRGB(0x0000ff);
  if(pressed == 3) {
    GD.Vertex2ii(280,34,BUTTON1_HANDLE);
    offset3=4;
    reversing = true;
  }else{
    GD.Vertex2ii(280,30,BUTTON0_HANDLE);
    offset3=0;
    reversing=false;
  }  
  GD.ColorRGB(0xffffff);
  GD.cmd_text(370, 45+offset3, 29, OPT_CENTERX,"Reverse");
  
  if(running)
    GD.cmd_spinner(130,110,1,0);
    
  GD.swap();
}

static void plotRate(int x, int y, int decimal, int fractional)
{
  int font = 31;
  
  GD.cmd_text(x,y-30,font-4,OPT_CENTER,"Rate:");
  GD.cmd_number(x - 8, y, font, OPT_RIGHTX | OPT_CENTERY, decimal);
  //GD.cmd_text(  x,     y, font, 0 | OPT_CENTERY, ".");
  
  GD.cmd_number(x + 8, y, font-1, 2 | OPT_CENTERY, fractional);
  GD.cmd_text(x+60,    y, font-2,OPT_CENTERY, "mL/hr");
  
  GD.PointSize(16 * 5); // means 30 pixels 
  GD.Begin(POINTS);
  GD.Vertex2ii(x, y);
}

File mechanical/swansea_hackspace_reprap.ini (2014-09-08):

[profile]
layer_height = 0.2
wall_thickness = 1.0
retraction_enable = True
solid_layer_thickness = 0.6
fill_density = 20
nozzle_size = 0.5
print_speed = 50
print_temperature = 200
print_temperature2 = 0
print_temperature3 = 0
print_temperature4 = 0
print_bed_temperature = 60
support = None
platform_adhesion = None
support_dual_extrusion = Both
wipe_tower = False
wipe_tower_volume = 15
ooze_shield = False
filament_diameter = 1.75
filament_diameter2 = 0
filament_diameter3 = 0
filament_diameter4 = 0
filament_flow = 100.0
retraction_speed = 40.0
retraction_amount = 4.5
retraction_dual_amount = 16.5
retraction_min_travel = 1.5
retraction_combing = True
retraction_minimal_extrusion = 0.02
retraction_hop = 0.0
bottom_thickness = 0.3
layer0_width_factor = 100
object_sink = 0.0
overlap_dual = 0.15
travel_speed = 150
bottom_layer_speed = 20
infill_speed = 0.0
inset0_speed = 0.0
insetx_speed = 0.0
cool_min_layer_time = 5
fan_enabled = True
skirt_line_count = 1
skirt_gap = 3.0
skirt_minimal_length = 150.0
fan_full_height = 0.5
fan_speed = 100
fan_speed_max = 100
cool_min_feedrate = 10
cool_head_lift = False
solid_top = True
solid_bottom = True
fill_overlap = 15
support_type = Grid
support_angle = 60
support_fill_rate = 15
support_xy_distance = 0.7
support_z_distance = 0.15
spiralize = False
simple_mode = False
brim_line_count = 20
raft_margin = 5.0
raft_line_spacing = 3.0
raft_base_thickness = 0.3
raft_base_linewidth = 1.0
raft_interface_thickness = 0.27
raft_interface_linewidth = 0.4
raft_airgap = 0.22
raft_surface_layers = 2
fix_horrible_union_all_type_a = True
fix_horrible_union_all_type_b = False
fix_horrible_use_open_bits = False
fix_horrible_extensive_stitching = False
plugin_config = 
object_center_x = -1
object_center_y = -1

[alterations]
start.gcode = ;Sliced at: {day} {date} {time}
	;Basic settings: Layer height: {layer_height} Walls: {wall_thickness} Fill: {fill_density}
	;Print time: {print_time}
	;Filament used: {filament_amount}m {filament_weight}g
	;Filament cost: {filament_cost}
	;M190 S{print_bed_temperature} ;Uncomment to add your own bed temperature line
	;M109 S{print_temperature} ;Uncomment to add your own temperature line
	G21        ;metric values
	G90        ;absolute positioning
	M82        ;set extruder to absolute mode
	M107       ;start with the fan off
	G28 X0 Y0  ;move X/Y to min endstops
	G28 Z0     ;move Z to min endstops
	G1 Z15.0 F{travel_speed} ;move the platform down 15mm
	G92 E0                  ;zero the extruded length
	G1 F200 E3              ;extrude 3mm of feed stock
	G92 E0                  ;zero the extruded length again
	G1 F{travel_speed}
	;Put printing message on LCD screen
	M117 Printing...
end.gcode = ;End GCode
	M104 S0                     ;extruder heater off
	M140 S0                     ;heated bed heater off (if you have it)
	G91                                    ;relative positioning
	G1 E-1 F300                            ;retract the filament a bit before lifting the nozzle, to release some of the pressure
	G1 Z+0.5 E-5 X-20 Y-20 F{travel_speed} ;move Z up a bit and retract filament even more
	G28 X0 Y0                              ;move X/Y to min endstops, so the head is out of the way
	M84                         ;steppers off
	G90                         ;absolute positioning
	;{profile_string}
start2.gcode = ;Sliced at: {day} {date} {time}
	;Basic settings: Layer height: {layer_height} Walls: {wall_thickness} Fill: {fill_density}
	;Print time: {print_time}
	;Filament used: {filament_amount}m {filament_weight}g
	;Filament cost: {filament_cost}
	;M190 S{print_bed_temperature} ;Uncomment to add your own bed temperature line
	;M104 S{print_temperature} ;Uncomment to add your own temperature line
	;M109 T1 S{print_temperature2} ;Uncomment to add your own temperature line
	;M109 T0 S{print_temperature} ;Uncomment to add your own temperature line
	G21        ;metric values
	G90        ;absolute positioning
	M107       ;start with the fan off
	G28 X0 Y0  ;move X/Y to min endstops
	G28 Z0     ;move Z to min endstops
	G1 Z15.0 F{travel_speed} ;move the platform down 15mm
	T1                      ;Switch to the 2nd extruder
	G92 E0                  ;zero the extruded length
	G1 F200 E10             ;extrude 10mm of feed stock
	G92 E0                  ;zero the extruded length again
	G1 F200 E-{retraction_dual_amount}
	T0                      ;Switch to the first extruder
	G92 E0                  ;zero the extruded length
	G1 F200 E10             ;extrude 10mm of feed stock
	G92 E0                  ;zero the extruded length again
	G1 F{travel_speed}
	;Put printing message on LCD screen
	M117 Printing...
end2.gcode = ;End GCode
	M104 T0 S0                     ;extruder heater off
	M104 T1 S0                     ;extruder heater off
	M140 S0                     ;heated bed heater off (if you have it)
	G91                                    ;relative positioning
	G1 E-1 F300                            ;retract the filament a bit before lifting the nozzle, to release some of the pressure
	G1 Z+0.5 E-5 X-20 Y-20 F{travel_speed} ;move Z up a bit and retract filament even more
	G28 X0 Y0                              ;move X/Y to min endstops, so the head is out of the way
	M84                         ;steppers off
	G90                         ;absolute positioning
	;{profile_string}
start3.gcode = ;Sliced at: {day} {date} {time}
	;Basic settings: Layer height: {layer_height} Walls: {wall_thickness} Fill: {fill_density}
	;Print time: {print_time}
	;Filament used: {filament_amount}m {filament_weight}g
	;Filament cost: {filament_cost}
	;M190 S{print_bed_temperature} ;Uncomment to add your own bed temperature line
	;M104 S{print_temperature} ;Uncomment to add your own temperature line
	;M109 T1 S{print_temperature2} ;Uncomment to add your own temperature line
	;M109 T0 S{print_temperature} ;Uncomment to add your own temperature line
	G21        ;metric values
	G90        ;absolute positioning
	M107       ;start with the fan off
	G28 X0 Y0  ;move X/Y to min endstops
	G28 Z0     ;move Z to min endstops
	G1 Z15.0 F{travel_speed} ;move the platform down 15mm
	T2                      ;Switch to the 2nd extruder
	G92 E0                  ;zero the extruded length
	G1 F200 E10             ;extrude 10mm of feed stock
	G92 E0                  ;zero the extruded length again
	G1 F200 E-{retraction_dual_amount}
	T1                      ;Switch to the 2nd extruder
	G92 E0                  ;zero the extruded length
	G1 F200 E10             ;extrude 10mm of feed stock
	G92 E0                  ;zero the extruded length again
	G1 F200 E-{retraction_dual_amount}
	T0                      ;Switch to the first extruder
	G92 E0                  ;zero the extruded length
	G1 F200 E10             ;extrude 10mm of feed stock
	G92 E0                  ;zero the extruded length again
	G1 F{travel_speed}
	;Put printing message on LCD screen
	M117 Printing...
end3.gcode = ;End GCode
	M104 T0 S0                     ;extruder heater off
	M104 T1 S0                     ;extruder heater off
	M104 T2 S0                     ;extruder heater off
	M140 S0                     ;heated bed heater off (if you have it)
	G91                                    ;relative positioning
	G1 E-1 F300                            ;retract the filament a bit before lifting the nozzle, to release some of the pressure
	G1 Z+0.5 E-5 X-20 Y-20 F{travel_speed} ;move Z up a bit and retract filament even more
	G28 X0 Y0                              ;move X/Y to min endstops, so the head is out of the way
	M84                         ;steppers off
	G90                         ;absolute positioning
	;{profile_string}
start4.gcode = ;Sliced at: {day} {date} {time}
	;Basic settings: Layer height: {layer_height} Walls: {wall_thickness} Fill: {fill_density}
	;Print time: {print_time}
	;Filament used: {filament_amount}m {filament_weight}g
	;Filament cost: {filament_cost}
	;M190 S{print_bed_temperature} ;Uncomment to add your own bed temperature line
	;M104 S{print_temperature} ;Uncomment to add your own temperature line
	;M109 T2 S{print_temperature2} ;Uncomment to add your own temperature line
	;M109 T1 S{print_temperature2} ;Uncomment to add your own temperature line
	;M109 T0 S{print_temperature} ;Uncomment to add your own temperature line
	G21        ;metric values
	G90        ;absolute positioning
	M107       ;start with the fan off
	G28 X0 Y0  ;move X/Y to min endstops
	G28 Z0     ;move Z to min endstops
	G1 Z15.0 F{travel_speed} ;move the platform down 15mm
	T3                      ;Switch to the 4th extruder
	G92 E0                  ;zero the extruded length
	G1 F200 E10             ;extrude 10mm of feed stock
	G92 E0                  ;zero the extruded length again
	G1 F200 E-{retraction_dual_amount}
	T2                      ;Switch to the 3th extruder
	G92 E0                  ;zero the extruded length
	G1 F200 E10             ;extrude 10mm of feed stock
	G92 E0                  ;zero the extruded length again
	G1 F200 E-{retraction_dual_amount}
	T1                      ;Switch to the 2nd extruder
	G92 E0                  ;zero the extruded length
	G1 F200 E10             ;extrude 10mm of feed stock
	G92 E0                  ;zero the extruded length again
	G1 F200 E-{retraction_dual_amount}
	T0                      ;Switch to the first extruder
	G92 E0                  ;zero the extruded length
	G1 F200 E10             ;extrude 10mm of feed stock
	G92 E0                  ;zero the extruded length again
	G1 F{travel_speed}
	;Put printing message on LCD screen
	M117 Printing...
end4.gcode = ;End GCode
	M104 T0 S0                     ;extruder heater off
	M104 T1 S0                     ;extruder heater off
	M104 T2 S0                     ;extruder heater off
	M104 T3 S0                     ;extruder heater off
	M140 S0                     ;heated bed heater off (if you have it)
	G91                                    ;relative positioning
	G1 E-1 F300                            ;retract the filament a bit before lifting the nozzle, to release some of the pressure
	G1 Z+0.5 E-5 X-20 Y-20 F{travel_speed} ;move Z up a bit and retract filament even more
	G28 X0 Y0                              ;move X/Y to min endstops, so the head is out of the way
	M84                         ;steppers off
	G90                         ;absolute positioning
	;{profile_string}
support_start.gcode = 
support_end.gcode = 
cool_start.gcode = 
cool_end.gcode = 
replace.csv = 
preswitchextruder.gcode = ;Switch between the current extruder and the next extruder, when printing with multiple extruders.
	;This code is added before the T(n)
postswitchextruder.gcode = ;Switch between the current extruder and the next extruder, when printing with multiple extruders.
	;This code is added after the T(n)

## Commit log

2014-01-25 Added simple extruder
    [extruder_print_all_v3.stl]
2014-01-25 Added syringe picture
2014-01-25 Removed holes.
    [extruder_print_all_v3.stl]
2014-01-25 Added holes again.
    [extruder_print_all_v3.stl]
2014-01-26 Another view of the syringe
2014-01-26 Arduino stepper motor code
2014-01-26 Moved pump code to main folder
2014-05-12 Recreated the Adafruit stepper motor setup.
    [stepper_arduino.fzz]
2014-06-18 added OSHW logo to PCB
    [stepper_arduino.fzz]
2014-08-22 Deleted old pump code
2014-09-02 Added stepper code
2014-09-02 Move stepper code into UI
2014-09-02 Added rotary encoder; stepper now with no delay
2014-09-08 Rearranging content and simplifying
    [extruder_print_all_v3.stl, linear_actuator_v0.scad]
2014-09-08 Added licenses
    [stepper_arduino.fzz]
2014-09-08 Made M3 nuts in syringe clamp a bit smaller
    [linear_actuator_v0.scad]
2014-09-08 Described 3D rendering procedure in more detail
    [linear_actuator_v0.scad]
2014-09-09 Breadboarded Pololu, Arduino and stepper
    [pololu_arduino.fzz]
2014-09-09 Circuit schematic for Arduino, stepper and driver
    [pololu_arduino.fzz]
2014-09-09 Updated Readme to include Fritzing
    [stepper_arduino.fzz]
2014-09-09 Changed label for DRV8834
    [pololu_arduino.fzz]
2014-09-10 Added Arduino library install instructions.
2014-09-25 Made attribution to MOST pump clearer
2014-10-15 Experimenting with ideas for enclosure
    [snap.dxf, test.scad]
2014-10-15 Pump shield to replace breadboard
    [pump-shield.fzz]
2014-10-16 Finalised schematic; now use sourceable components
    [pump-shield.fzz, pump-shield_contour.gm1, pump-shield_copperBottom.gbl, pump-shield_copperTop.gtl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]
2014-10-17 Generated new berbers
    [pump-shield.fzz, pump-shield_contour.gm1, pump-shield_copperBottom.gbl, pump-shield_copperTop.gtl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]
2014-10-17 Moved some labels
    [pump-shield.fzz]
2014-10-17 Fixed openpump logo
    [pump-shield.fzz, pump-shield_contour.gm1, pump-shield_silkBottom.gbo, pump-shield_silkTop.gto]
2014-10-20 Version sent off to fab
    [pump-shield.fzz, pump-shield_silkTop.gto]
2014-10-30 Started on OpenSCAD model for enclosure
    [arduino.scad, pins.scad]
2014-10-31 First test print of enclosure
    [arduino.scad, scadModel.stl]
2014-11-06 Added side supports
    [arduino.scad]
2014-11-06 STL now with side supports
    [scadModel.stl]
2014-11-07 Swopped right way round
    [arduino.scad]
2014-11-07 Small test print for location of screen
    [arduino.scad]
2014-11-07 making lid
    [arduino.scad]
2014-11-07 First print of enclosure
    [arduino.scad, scadModel.stl]
2014-11-07 Lid before cutout
    [arduino.scad]
2014-11-07 With cutout
    [arduino.scad]
2014-11-07 Cutouts for encoder and cables
    [rotary.dxf]
2014-11-07 Enclosure iteration 3
    [arduino.scad]
2014-11-07 Lid iteration 1
    [arduino.scad]
2014-11-09 Changed direction/step pins for Pump Shield v0.1
2014-11-09 Moved prism, enclosure and cable cutouts
    [arduino.scad]
2014-11-09 Changed screen cutout size and removed lip
    [arduino.scad]
2014-11-13 Changed encoder panel from prism to cube
    [arduino.scad, openPumpBox.stl, openPumpLid.stl]
2014-11-19 Added how-to use description
    [arduino.scad]
2015-03-06 Added .stl files for printing
    [1_end_motor.stl, 2_end_idler.stl, 4_carriage_syringe_pump.stl, 5_clamp_syringe_pump.stl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]

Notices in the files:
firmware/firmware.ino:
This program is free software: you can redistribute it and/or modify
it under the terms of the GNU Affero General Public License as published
